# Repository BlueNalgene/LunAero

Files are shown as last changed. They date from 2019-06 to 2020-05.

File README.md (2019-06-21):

The first fully automated lunar bird tracker

# LunAero
LunAero is a hardware and software project using OpenCV to automatically track birds as they migrate in front of the moon.  This repository contains information related to the construction of LunAero hardware and the software required for running the moon tracking program.  Bird detection has "migrated" to a new repository at https://github.com/BlueNalgene/Birdtracker_LunAero.

Created by @BlueNalgene, working in the lab of @Eli-S-Bridge.

## Hardware Recommendations

- Computer (see notes)
- Camera (see notes)
- Motors (2)
- TB6612FNG motor controller
- 1/4" Acrylic (about 18"x24")
- 1/8" Acetal (about 3"x3")
- Screws and Wires

For best results, we recommend running this on a Linux computer with USB 3 slots.  For a low cost option, the ODROID N2 single board computer has been found to be effective.  The installation instructions in this README are based on that hardware.

A hard drive capable of storing data at high transfer rates is required.  This can take the form of USB 3 compliant memory device, the ODROID eMMC modules, or a SATA drive.  For cost reasons, we recommend the eMMC module, and have found it to be effective.

This installation uses a USB 3 CCD camera.  Customization can be made for other cameras which use other interfaces, such as a CSI MIPI port.  Feel free to contact the repo maintainer if you are interested in this and need some help implementing it.

A TB6612FNG breakout board is required to control two motors.  If you don't have one of these laying around (we made our own board in house), you can get them from Sparkfun https://www.sparkfun.com/products/14451.

This hardware implementation requires two low speed/high torque 5V motors.  We used 0.5 rpm motors purchased from Amazon (uxcell DC 5V 0.5RPM Worm Gear Motor 6mm Shaft High Torque Turbine Reducer).  If you change motors, be sure that the CAD designs match the drill holes required for the motor to attach to the plastic.

This project include designs for plastic parts to be cut from 1/4" acrylic plastic and 1/8" acetal plastic.  You can change these materials if you like.  E.g. it would be reasonable to swap the acetal for some of the 1/4" acyrlic if you are low on funds.  HOWEVER, the acetal makes much better gears and will give you much smoother motion.

You also need a bunch of bolts and screws and whatnot.  One of these days I will measure the ones I used and report back with numbers.

## Using the 2D CAD files

The CAD files in the 2D CAD folder are used to construct parts for LunAero including gears and mounting brackets.  The parts are designed to be cut on a laser CNC machine.  They can also be used as templates for cutting on a band saw or using another CNC machine.

The units are in mm for all parts.

Assembly information will be provided in the 2D CAD subfolder dedicated for that purpose.

### USB 3 and LunAero

Why is USB 3 so important?  The data lanes on USB 2 and below are too small for what we need.  In order to record and process footage at a high frame rate (~30 fps) and large image size (1920x1080), we need to move 187 Mb/s.  USB 2 is only capable of 60 Mb/s.  This means that if we try to record from a USB 2 connection, we will lose frames and data.  Eventually, the extra data we are trying to push through the small pipe will overrun (as our tests demonstrated empirically), and some major lag will occur in the tracking.  This has often caused early LunAero prototypes to lose the moon while attempting to track it.

## Software Install Instructions
When you install this for the first time on to a 'blank' ODROID N2, you will need to use `git` to pull this repository.  Then you can pull everything in and run it.  To do this, execute the lines in the terminal (ctrl+alt+t):
```
sudo apt update
sudo apt -y install git
git clone https://github.com/BlueNalgene/LunAero.git
cd LunAero
```

This script downloads the `git` program and then pulls in the repository posted here.  Once you have the repo on your N2, you go into the folder, then execute the install script.  This should take less than a minute on a modern internet connection.

```
sudo ./ODROID_INSTALL.sh
```

When the INSTALL script is executed, it will go through all of the dependencies you need for this program.  If you don't have them installed, it will do that for you.  Note that this **TAKES A LONG TIME**.  You have been warned.

When you are finished, you can copy the desktop file to the N2's desktop and you will be ready to go.

```
cp ./odroid_moontracker.desktop /home/odroid/Desktop
```

## Running LunAero

Double-click the desktop icon you made for LunAero.  This will open a window with a very simple graphical user interface.

### Time Confirmation

The first screen will ask you to check the time.  LunAero calculations are performed by referencing the system time of the computer you are using.  Check to see that the time displayed on the screen is accurate against another known source (e.g. your watch or phone).  If the time is correct, select `y` and you will move on to the next mode.  Otherwise, you will enter in the date and time for your location in the next series of prompts using 2 digit entries, pressing enter each time.  Example: If you were witness to the meteor impact on the moon which occurred on September 11th 2013 at 8:07:28 PM UTC, you would type:

```
13
[enter]
09
[enter]
11
[enter]
20
[enter]
07
[enter]
28
[enter]
```

Select the correct time zone.  The only available options right now are in North America.  For international users, please use UTC time.

This will not change the system time of your computer.  There are other ways to do that, and I won't go into them here.  This just tells LunAero what time you started recording.

### Manual Adjustment Mode

Once you have confirmed the time is correct in LunAero, you will enter the manual tracking mode.  This is a screen that shows a video feed from the camera in the top right corner of the screen.  You can move the scope around with arrow keys, and adjust some camera parameters.

Move the scope position such that it is looking at the moon.  There will be a red ellipse on drawn on the screen.  Try to get the size of the moon in the viewer to match that circle by adjusting the zoom of your scope.

Adjust the camera settings (mostly the "exposure" value) such that you are able to see all of the craters of the moon as crisp as possible, while making sure the view is not too dark.  Empirically, we found that this is an exposure setting between 5-100 units.  There is a special key that adjusts the settings to where I personally had the best results, and this makes for a good reference point.

Check the "computer vision" version of the image by pressing `v`.  This will show a black and white image in the lower right hand corner of the screen.  This is what LunAero "sees".  Make sure that it can see the entirety of the moon.  If the computer vision just shows part of what you can see in the normal view, you may have set the exposure too low.

### Automatic Mode

Once you are happy with the settings, press `Enter` or `r` to run the automatic mode.  Then step away.  Watch with joy and wonder as the scope automatically follows the moon as it moves across the sky.  LunAero is recording everything that happens in view of the scope now.  You can walk away from it and it will continue recording.  Be sure to check that the weather is good and you are in a secure location.  Members of the LunAero team are not responsible for anything that happens to your scope if left outside during inclement weather or sticky fingers.

## Bird Detection Software

As of June 21st, 2019, the software for tracking birds in video of the moon has been migrated to a new repository at https://github.com/BlueNalgene/Birdtracker_LunAero.  The repo now only contains the hardware information and the software required to run the moon tracking program and record video.

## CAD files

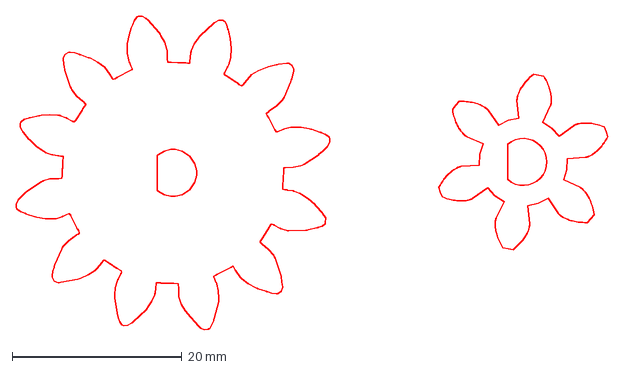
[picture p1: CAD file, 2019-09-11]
2D_CAD/LunAero_acetal_gear_metric.dxf
69.8 x 37.0 mm

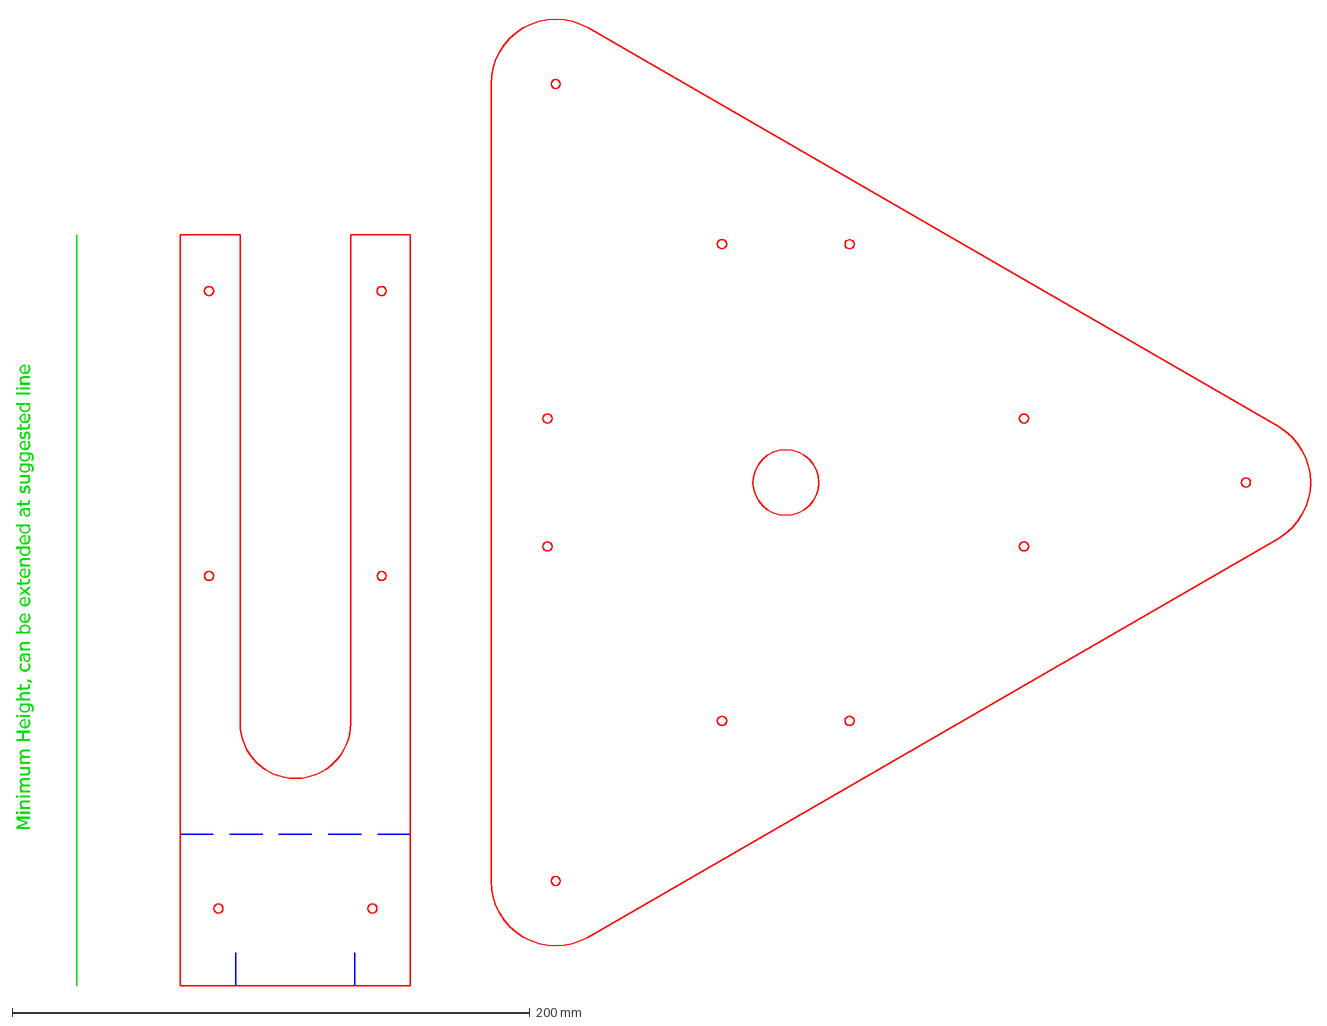
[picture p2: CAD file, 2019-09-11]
2D_CAD/MoonWatcher_wood1inch.dxf
Minimum Height, can be extended at suggested line

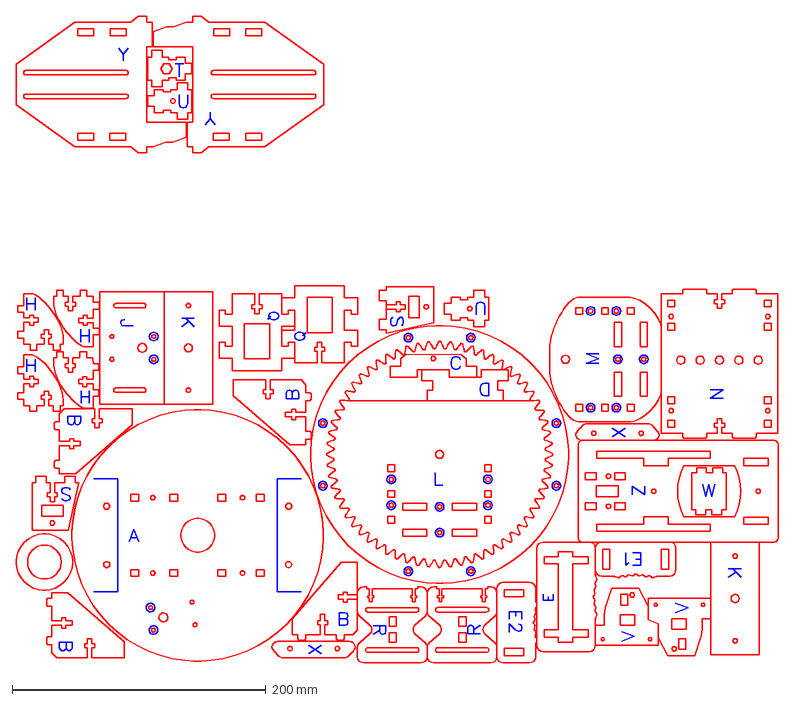
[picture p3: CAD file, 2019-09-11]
2D_CAD/MoonWatcher_0.225in.dxf
600.5 x 509.8 mm

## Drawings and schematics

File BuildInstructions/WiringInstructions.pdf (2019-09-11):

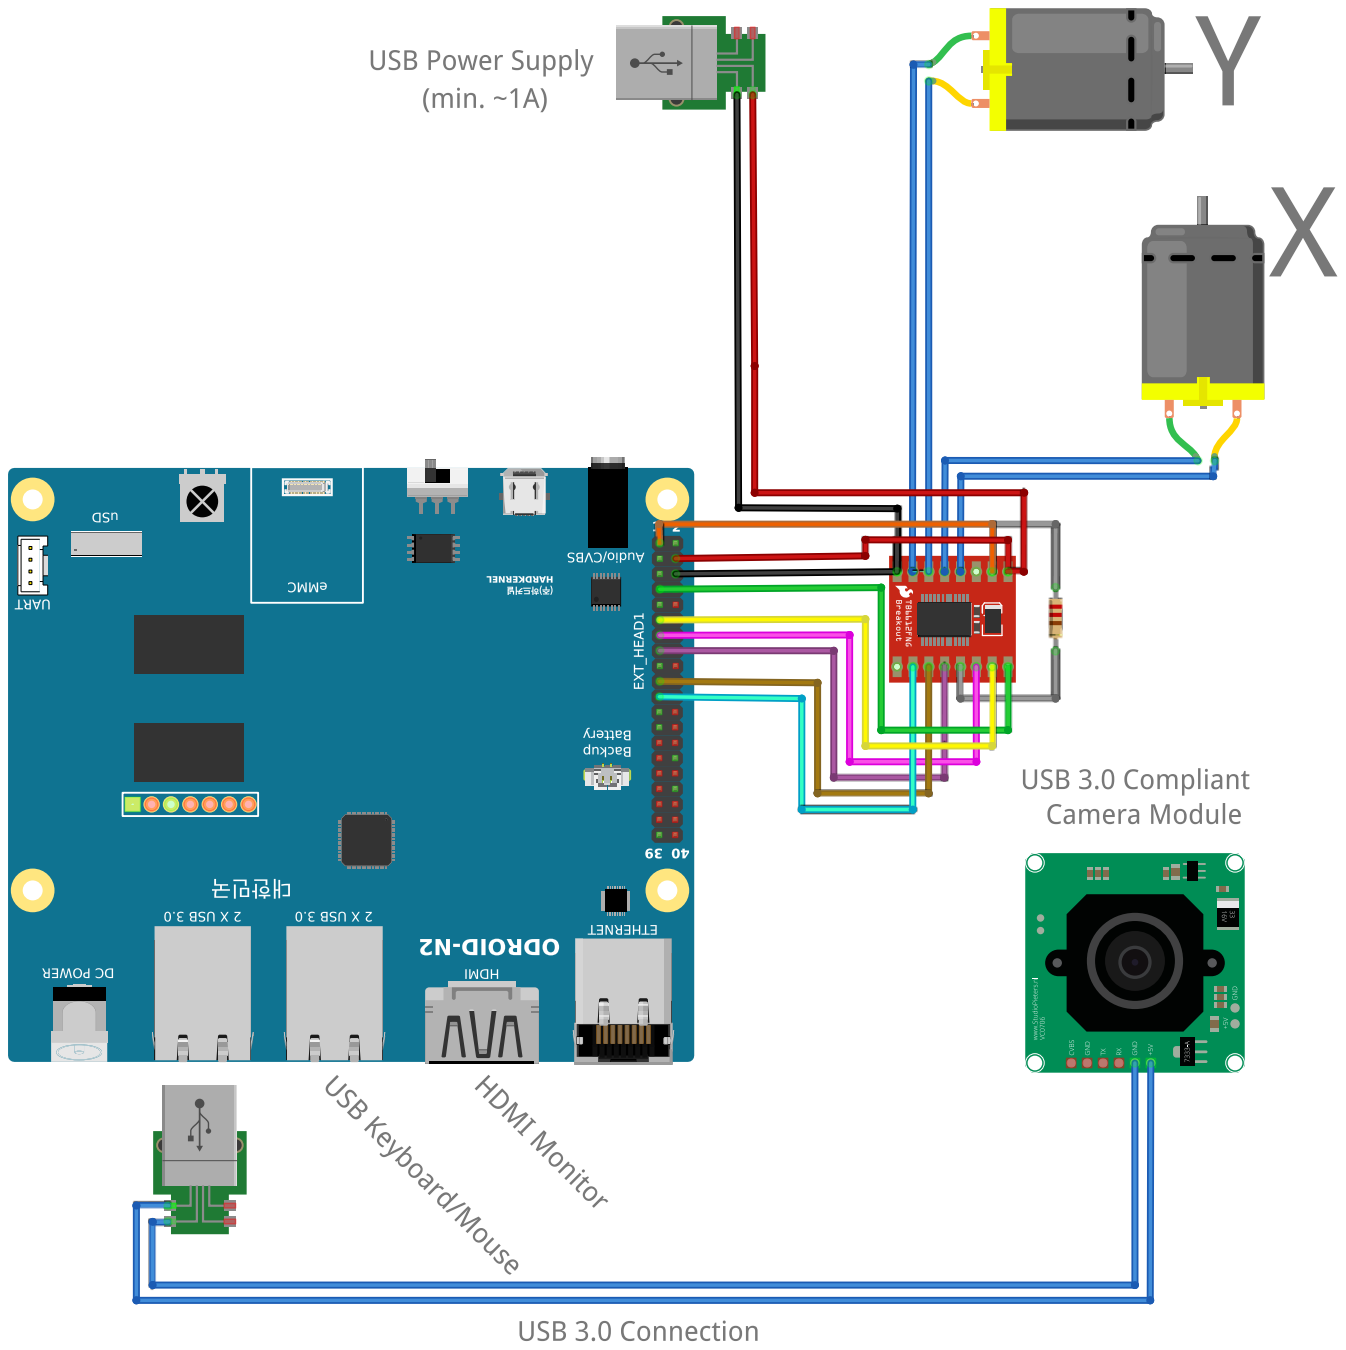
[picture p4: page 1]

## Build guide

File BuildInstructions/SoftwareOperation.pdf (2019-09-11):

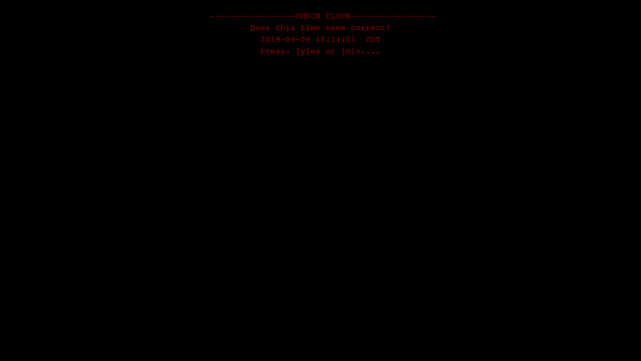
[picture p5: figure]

When the moontracker program is first opened, the user will be asked to verify the time provided by the system clock. If the time is correct, press [y] to proceed to the manual moon finding phase. If it is incorrect, press [n].

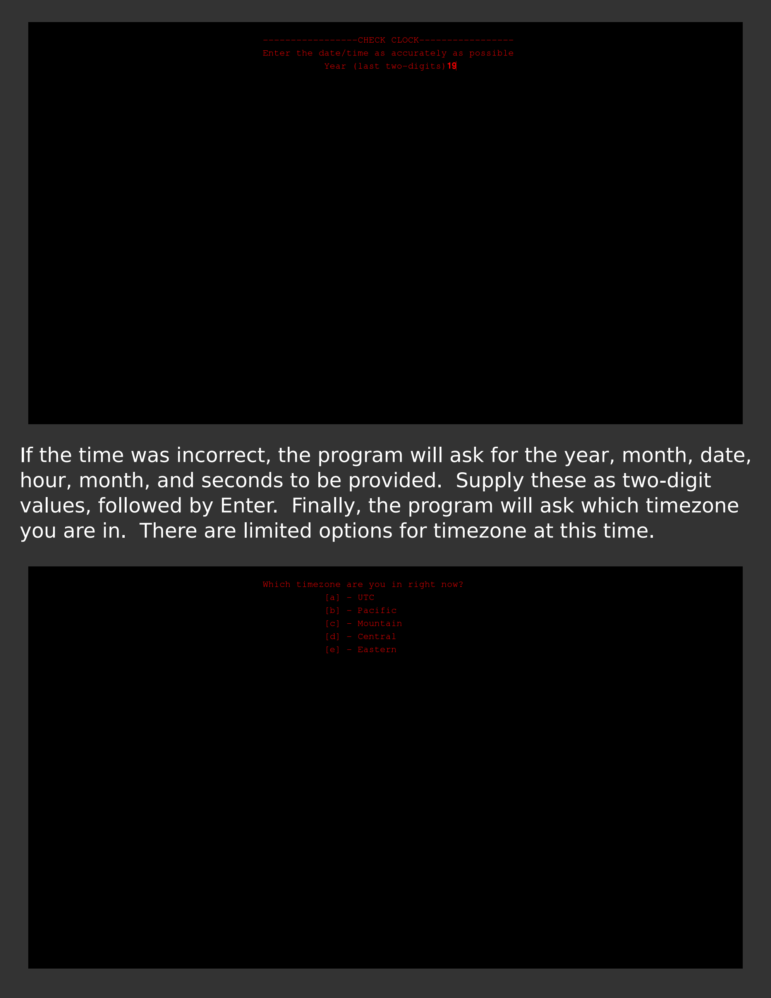
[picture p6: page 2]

If the time was incorrect, the program will ask for the year, month, date, hour, month, and seconds to be provided. Supply these as two-digit values, followed by Enter. Finally, the program will ask which timezone you are in. There are limited options for timezone at this time.

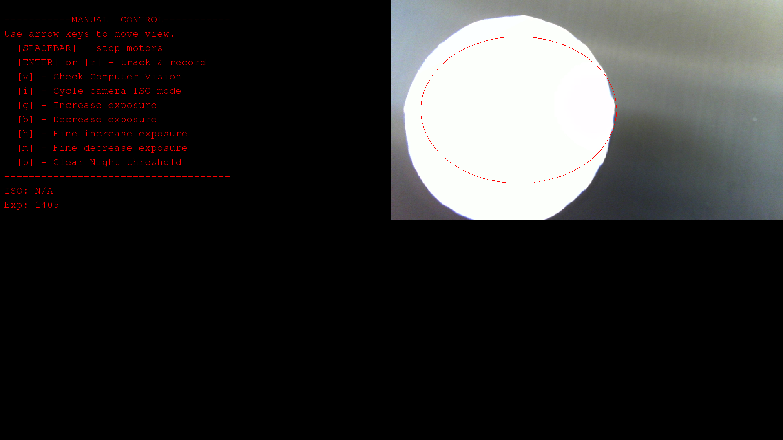
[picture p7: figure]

Once the program reaches the Manual Control screen, the moon must be brought into view of the screen. Use the arrow keys to manually adjust the position of the turret altitude and azimuth until the moon
is visible on the screen. A red oval or circle serves as a targeting reticle for optimum position.

Once the moon is visible on the screen, confirm that the entire moon fits in the visible window. Adjust the zoom and focus of your spotting scope to achieve sharp edges.

When the moon is first found by the program, the exposure settings of the camera will be set such that the moon appears "washed-out" or overly bright. This is intentional. Finding the moon through the scope can be challenging, and the glow of the over-exposed haze around the moon can aid in the initial positioning.

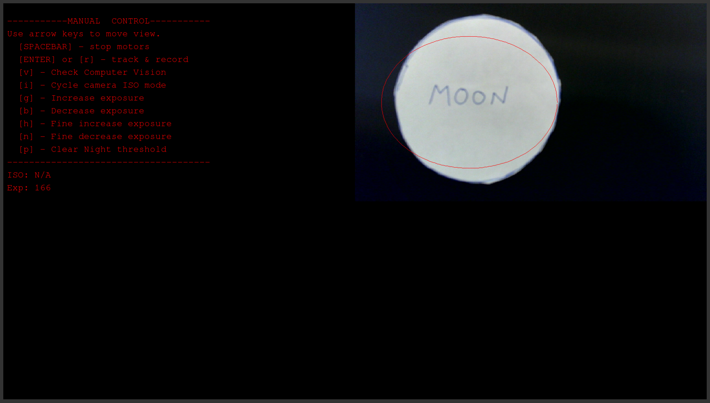
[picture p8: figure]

Once the moon is properly positioned in the frame, adjust the ISO and exposure settings of the camera such that the edges of the craters of the moon are visible and detailed. In the high-quality demo image above, adjusting the settings make the word "MOON" visible.

The ISO of the camera is cycled with [i]. This option will not be available with all cameras.

The exposure setting of the camera has coarse and fine adjustments. The keys to increase and decrease the exposure value are [g] and [b] for coarse adjustments and [h] and [n] for fine adjustments, respectively.

An optimized setting activated with [p] can be performed. This automatically sets the exposure value to what has been empirically determined by the authors to be "good". This can make for a nice starting point before making fine adjustments.

Press [v] to bring up a black and white image in the bottom right. This is what the computer vision "sees".

When everything is ready, press Enter or [r] to proceed to auto tracking mode.

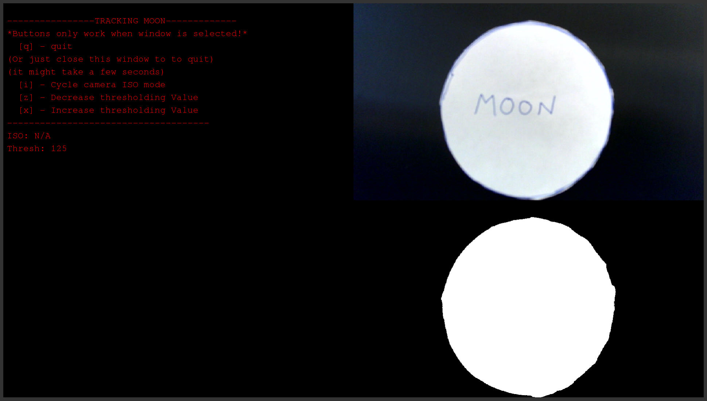
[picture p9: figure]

In the automated tracking mode, LunAero will operate independently of the user. Few settings can be changed once in auto mode. If ISO is enabled by the camera hardware, that can be cycled here. However, exposure values cannot change.

When the moon is centered during proper function, threshold images will pop up on the screen for debugging purposes in the lower-right quadrant of the screen. As before, the image here represents what the tracking software "sees" when determining how to center the moon in frame.

If a change in site conditions causes the moon to be dim or overlybright on the screen, the black and white threshold can be adjusted by pressing [z] or [x]. Adjusting this threshold value is only able to change how LunAero "sees" the moon when centering. It will not effect recorded video. If you temporarily lose the moon due to haze, changing the BW threshold can allow you to continue tracking the moon.

When the moon is lost, the program will shut down automatically. To manually quit, press [q].

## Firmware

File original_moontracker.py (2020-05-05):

"""
Motor control and recording for Lunaero

Motor A is up and down
Motor B is right and left
"""

# Standard imports
import io
import multiprocessing as mp
import os
import os.path
import subprocess
import sys
import threading
import time

# Non-standard imports
import cv2
import pygame

# Third Party imports
import numpy as np

# Special Mode Imports
from _datetime import datetime

# Local Imports

#position = (620, 20)
#os.environ['SDL_VIDEO_WINDOW_POS'] = str(position[0]) + "," + str(position[1])
pygame.display.init()
pygame.font.init()

# Get information for the current screen size.
SWID, SHEI = pygame.display.Info().current_w, pygame.display.Info().current_h
# Convert to the size of each quadrant of the screen
QWID = int(SWID/2)
QHEI = int(SHEI/2)

#white = (255, 255, 255)
RED = (255, 0, 0)
FONT = pygame.font.SysFont('monospace', 25)

SCREEN = pygame.display.set_mode((SWID, SHEI))

# Enable blind mode while tracking.
# True = don't display tracking window to save cpu cycles
# False = display visuals (default)
BLIND = False

# Select the device you are using.
# Raspberry Pi with Raspberry Pi Camera: 0
# Linux Computer with USB Camera: 1
# WiringPi Compatible Computer (Odroid N2) with USB Camera: 2
# WiringPi Compatible Computer (Odroid N2) with ActionCam: 3
# Raspberry Pi with ActionCam: 4
# TODO detect hardware
DEV = 0

#Enable logs with True, disable with False:
LOGS = False

#Asychronous Recording
ASYNC = True


class TextInput:
	"""
	Copyright 2017, Silas Gyger, silasgyger@gmail.com, All rights reserved.
	Borrowed from https://github.com/Nearoo/pygame-text-input under the MIT license.
	This class lets the user input a piece of text, e.g. a name or a message.
	This class let's the user input a short, one-lines piece of text at a blinking cursor
	that can be moved using the arrow-keys. Delete, home and end work as well.
	"""
	def __init__(self, initial_string="", font_family="", font_size=35, antialias=True, \
		text_color=(255, 0, 0), cursor_color=(127, 0, 0), repeat_keys_initial_ms=400, \
			repeat_keys_interval_ms=35):
		"""
		:param initial_string: Initial text to be displayed
		:param font_family: name or list of names for font (see pygame.font.match_font
		for precise format)
		:param font_size:  Size of font in pixels
		:param antialias: Determines if antialias is applied to font (uses more processing power)
		:param text_color: Color of text (duh)
		:param cursor_color: Color of cursor
		:param repeat_keys_initial_ms: Time in ms before keys are repeated when held
		:param repeat_keys_interval_ms: Interval between key press repetition when helpd
		"""
		# Text related vars:
		self.antialias = antialias
		self.text_color = text_color
		self.font_size = font_size
		self.input_string = initial_string  # Inputted text
		# Fonts
		if not os.path.isfile(font_family):
			font_family = pygame.font.match_font(font_family)
		self.font_object = pygame.font.Font(font_family, font_size)
		# Text-surface will be created during the first update call:
		self.surface = pygame.Surface((1, 1))
		self.surface.set_alpha(0)
		# Vars to make keydowns repeat after user pressed a key for some time:
		self.keyrepeat_counters = {}  # {event.key: (counter_int, event.unicode)} (look for "***")
		self.keyrepeat_intial_interval_ms = repeat_keys_initial_ms
		self.keyrepeat_interval_ms = repeat_keys_interval_ms
		# Things cursor:
		self.cursor_surface = pygame.Surface((int(self.font_size/20+1), self.font_size))
		self.cursor_surface.fill(cursor_color)
		self.cursor_position = len(initial_string)  # Inside text
		self.cursor_visible = True  # Switches every self.cursor_switch_ms ms
		self.cursor_switch_ms = 500  # /|\
		self.cursor_ms_counter = 0
		# Init clock
		self.clock = pygame.time.Clock()
	def update(self, events):
		"""Update the values in the box
		"""
		for event in events:
			if event.type == pygame.QUIT:
				sys.exit()
			if event.type == pygame.KEYDOWN:
				self.cursor_visible = True  # So the user sees where he writes
				# If none exist, create counter for that key:
				if event.key not in self.keyrepeat_counters:
					self.keyrepeat_counters[event.key] = [0, event.unicode]
				if event.key == pygame.K_BACKSPACE:
					self.input_string = (self.input_string[:max(self.cursor_position - 1, 0)] + \
						self.input_string[self.cursor_position:])
					# Subtract one from cursor_pos, but do not go below zero:
					self.cursor_position = max(self.cursor_position - 1, 0)
				elif event.key == pygame.K_DELETE:
					self.input_string = (self.input_string[:self.cursor_position] + \
						self.input_string[self.cursor_position + 1:])
				elif event.key == pygame.K_RETURN:
					print(str(self.input_string))
					return True
				elif event.key == pygame.K_RIGHT:
					# Add one to cursor_pos, but do not exceed len(input_string)
					self.cursor_position = min(self.cursor_position + 1, len(self.input_string))
				elif event.key == pygame.K_LEFT:
					# Subtract one from cursor_pos, but do not go below zero:
					self.cursor_position = max(self.cursor_position - 1, 0)
				elif event.key == pygame.K_END:
					self.cursor_position = len(self.input_string)
				elif event.key == pygame.K_HOME:
					self.cursor_position = 0
				else:
					# If no special key is pressed, add unicode of key to input_string
					self.input_string = (self.input_string[:self.cursor_position] + \
						event.unicode + self.input_string[self.cursor_position:])
					self.cursor_position += len(event.unicode)  # Some are empty, e.g. K_UP
			elif event.type == pygame.KEYUP:
				# *** Because KEYUP doesn't include event.unicode,
				#this dict is stored in such a weird way
				if event.key in self.keyrepeat_counters:
					del self.keyrepeat_counters[event.key]
		# Update key counters:
		for key in self.keyrepeat_counters:
			self.keyrepeat_counters[key][0] += self.clock.get_time()  # Update clock
			# Generate new key events if enough time has passed:
			if self.keyrepeat_counters[key][0] >= self.keyrepeat_intial_interval_ms:
				self.keyrepeat_counters[key][0] = (self.keyrepeat_intial_interval_ms - \
					self.keyrepeat_interval_ms)
				event_key, event_unicode = key, self.keyrepeat_counters[key][1]
				pygame.event.post(pygame.event.Event(pygame.KEYDOWN, key=event_key,\
					unicode=event_unicode))
		# Re-render text surface:
		self.surface = self.font_object.render(self.input_string, self.antialias, self.text_color)
		# Update self.cursor_visible
		self.cursor_ms_counter += self.clock.get_time()
		if self.cursor_ms_counter >= self.cursor_switch_ms:
			self.cursor_ms_counter %= self.cursor_switch_ms
			self.cursor_visible = not self.cursor_visible
		if self.cursor_visible:
			cursor_y_pos = self.font_object.size(self.input_string[:self.cursor_position])[0]
			# Without this, the cursor is invisible when self.cursor_position > 0:
			if self.cursor_position > 0:
				cursor_y_pos -= self.cursor_surface.get_width()
			self.surface.blit(self.cursor_surface, (cursor_y_pos, 0))
		self.clock.tick()
		return False
	def get_surface(self):
		"""
		Called to get the surface
		"""
		return self.surface
	def get_text(self):
		"""
		Called to get the text string
		"""
		return self.input_string
	def get_cursor_position(self):
		"""
		Called to get the cursor position
		"""
		return self.cursor_position
	def set_text_color(self, color):
		"""
		Called to set the color of the text
		"""
		self.text_color = color
	def set_cursor_color(self, color):
		"""
		Called to set the color of the mouse cursor
		"""
		self.cursor_surface.fill(color)
	def clear_text(self):
		"""
		Called to clear the text string.
		"""
		self.input_string = ""
		self.cursor_position = 0

class TimeLoop():
	"""
	This class contains screens which ask the user to verify the time listed on the raspberry pi.
	The intended use is to provide for instances when the pi is not able to auto sync the clock
	with an internet connection, yet not use an RTC.
	"""
	tix = TextInput()
	def __init__(self):
		"""
		:param startup: Toggle switch for while loop
		:param timetuple: Empty tuple to hold time values
		:param mrgn: Margin around text to act as padding
		:param ftsz: Font size in points
		"""
		self.startup = True
		self.timetuple = ()
		self.mrgn = 10
		self.ftsz = 25

	def firstcheck(self):
		"""
		Ask the user to confirm that the time is correct
		"""
		timetuple = ()
		while self.startup:
			SCREEN.fill((0, 0, 0))
			lctn = self.mrgn + self.ftsz
			hpos = QWID - 22*(self.ftsz-self.mrgn)
			SCREEN.blit(FONT.render('-----------------CHECK CLOCK-----------------', True, RED),\
				(hpos, lctn))
			lctn = lctn + self.ftsz + self.mrgn
			SCREEN.blit(FONT.render('        Does this time seem correct?         ', True, RED),\
				(hpos, lctn))
			lctn = lctn + self.ftsz + self.mrgn
			hpos = QWID - round(len(self.thetime())/2)*(self.ftsz-self.mrgn)
			SCREEN.blit(FONT.render(str(self.thetime()), True, RED), (hpos, lctn))
			lctn = lctn + self.ftsz + self.mrgn
			hpos = QWID - 22*(self.ftsz-self.mrgn)
			SCREEN.blit(FONT.render('          Press: [y]es or [n]o....           ', True, RED),\
				(hpos, lctn))
			pygame.display.update()
			events = pygame.event.get()
			for event in events:
				if event.type == pygame.QUIT:
					sys.exit()
				if event.type == pygame.KEYDOWN:
					if event.key == pygame.K_y:
						return True
					if event.key == pygame.K_n:
						if LOGS:
							print("changing time")
						pygame.time.wait(100)
						i = 0
						while i < 6:
							timetuple += (int(self.timeinput(i)),)
							i += 1
						# Add milliseconds
						timetuple += (0,)
						if LOGS:
							print(timetuple)
						while not self.tzpick():
							pass
						self.startup = not self.startup
		return timetuple

	def timeinput(self, ith):
		"""
		Pygame.  Constructs a tuple of date values to use when setting the date and time
		"""
		while True:
			SCREEN.fill((0, 0, 0))
			lctn = self.mrgn + self.ftsz
			hpos = QWID - 22*(self.ftsz-self.mrgn)
			SCREEN.blit(FONT.render('-----------------CHECK CLOCK-----------------', True, RED),\
				(hpos, lctn))
			lctn = lctn + self.ftsz + self.mrgn
			hpos = QWID - 22*(self.ftsz-self.mrgn)
			SCREEN.blit(FONT.render('Enter the date/time as accurately as possible', True, RED),\
				(hpos, lctn))
			lctn = lctn + self.ftsz + self.mrgn
			hpos = QWID - 11*(self.ftsz-self.mrgn)
			if ith == 0:
				SCREEN.blit(FONT.render('Year (last two-digits)', True, RED), (hpos, lctn))
			elif ith == 1:
				SCREEN.blit(FONT.render('Month (two-digits)', True, RED), (hpos, lctn))
			elif ith == 2:
				SCREEN.blit(FONT.render('Day (two-digits)', True, RED), (hpos, lctn))
			elif ith == 3:
				SCREEN.blit(FONT.render('Hour (two-digits)', True, RED), (hpos, lctn))
			elif ith == 4:
				SCREEN.blit(FONT.render('Minute (two-digits)', True, RED), (hpos, lctn))
			elif ith == 5:
				SCREEN.blit(FONT.render('Second (two-digits)', True, RED), (hpos, lctn))
			hpos = QWID + 11*(self.ftsz-self.mrgn)
			events = pygame.event.get()
			SCREEN.blit(self.tix.get_surface(), (hpos, lctn))
			if self.tix.update(events):
				outputstring = self.tix.get_text()
				if len(outputstring) == 2 and outputstring.isdigit():
					self.tix.clear_text()
					if ith == 0:
						outputstring = 2000 + int(outputstring)
					return outputstring
				else:
					self.badinput(lctn)
			pygame.display.update()
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

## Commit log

2018-03-12 removed folder of old stuff
    [Lunaero_cam1.stl, Lunaero_case1.stl, Lunaero_clamp1.stl, RasPiCameraAdapter.scad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]
2018-04-19 yesterday withincontour
    [#LunAero_CAD.dxf]
2018-04-21 updates to streaming and threading in simpletracker
2018-04-23 README update and framechecker.py
2018-04-23 framechecker fix
2018-05-07 Latest Eli Illustrator Files
    [#LunAero_CAD.dxf, LunAero_CAD.dxf]
2018-06-07 up to 2 frame detection
2018-06-20 working 3 frame dependent differences
2018-07-11 fixed MotorControl imports
2018-07-23 fixes to socket
2018-07-23 more sockets
2018-07-23 camera exposure
2018-07-31 client side fixes, socketing RAM image!
2018-08-01 more threading
2018-08-15 dxf file, separate thickness for thicker sheets
    [MoonWatcher.dxf, MoonWatcher_0.225in.dxf]
2018-09-14 commits from fall 2018 test
    [MoonWatcher.dxf, MoonWater_small_clamp_mod_0.225.dxf]
2018-09-14 saving frames as np layers
2018-11-13 corrected filename to reflect lack of Kalman filter
2018-11-15 fixed uncommented debug print line
2019-04-15 fix for no moon - skip the frame
2019-04-18 print iso/thresh/exp info on screen
2019-05-01 simple changes
    [MoonWatcher_0.225in.dxf]
2019-05-01 aluminum gear options, allows for kerf of .05in
    [MoonWatcher_0.225in_ALgears.dxf]
2019-05-01 Started making class files, controls for PCA9685 motor controller
2019-05-09 added capability to use more than two hardware devices
2019-05-09 wiringpi capable with DEV switch
2019-05-09 remove debug text, pythonic pins required for wiringpi
2019-05-13 USB 3.0 camera adapt
2019-05-15 restore old CAD files and add ELP only version
    [MoonWatcher_0.225in.dxf, MoonWatcher_0.225in_ELP.dxf]
2019-05-21 options added for USB 2 and USB 3 camera
2019-06-21 removed Raspberry Pi installation files
2019-08-26 Deleted via the Open Science Framework
2019-09-11 updates to prep for HX publication
    [LunAero_acetal_gear_metric.dxf, MoonWatcher_0.225in.dxf, MoonWatcher_wood1inch.dxf]
2019-10-08 cleaned up 2D files and ActionCam changes to original_moontracker started
    [MoonWatcher_0.225in_ALgears.dxf, MoonWatcher_0.225in_ELP.dxf, MoonWater_small_clamp_mod_0.225.dxf]
